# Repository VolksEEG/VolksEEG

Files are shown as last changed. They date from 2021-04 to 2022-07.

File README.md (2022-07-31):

# VolksEEG: Acheiving the Promise of Open Source Medical Devices

In a nutshell...

* *The VolksEEG project is creating an open-source
electroencephalogram (EEG) machine, fully-functional for clinical or research use.*

* *The final device will obtain clearance by the USA FDA, and CE marking
(the equivalent of FDA clearance in the EU).*

* *Currently, no other
open-source electronic medical device (that we know of) has full regulatory clearance*

* *All hardware and software designs will be freely available ([free as in speech and as in beer](https://www.howtogeek.com/howto/31717/what-do-the-phrases-free-speech-vs.-free-beer-really-mean)).*

VolksEEG will be the first in a line of open-source medical
devices that will enable a quantum leap in device safety, cost reduction, and innovation.

To sign up for updates about the project, head to [volkseeg.org](https://volkseeg.org).

Here is a video showing the real-time display of 32 waveform channels, from a UI proof-of-concept application:

<https://user-images.githubusercontent.com/58418/132131736-32bca075-f591-47dc-b3fa-c07dddc95de6.mp4>

(The final device will display EEG channels rather than sine waves, of course.)

## Qs & As

You might have a few questions; we have answers, click on the links below to read the:

* [Why are open-source medical devices a good
idea?](#why-are-open-source-medical-devices-a-good-idea)

* [Medical devices? Do you actually know what you're doing?](#do-you-actually-know-what-you-are-doing)

* [Why an EEG machine?](#why-start-with-an-eeg-machine)

* [What needs to be done?](#what-needs-to-be-done)

* [How can I help?](#how-can-i-help)

* [Project planning](#Project-planning)

* [Wait... don't medical devices need to have full requirements and specifications before starting any development?](#where-are-the-detailed-requirements-and-specs)

---

## Why are open-source medical devices a good idea?

Open-source medical devices will provide increased safety, increased
innovation, and reduced device costs.

### Increased Safety

Like all devices, medical devices have become much more complex over
time. *Unlike* all devices, medical devices are often safety- or
life-critical.

As complexity increases, it becomes ever easier to overlook
small design flaws during development, often leading to recalls
later – each year, hundreds of thousands of devices are subject to Class
I recalls, the FDA’s most serious class of recall, reserved for issues
that could cause serious injury or death.

Design flaws are detected by *design reviews*. A core challenge of medical
device safety is ensuring the adequacy of design reviews – both in the
person-hours spent, and the expertise of the reviewers. While design
reviews of proprietary medical devices typically involve only a handful
of reviewers, open-source devices can leverage the eyeballs of myriad
reviewers with a wide variety of expertise; as stated in *The Cathedral
and the Bazaar,* "given enough eyeballs, all bugs are shallow".

### Increased Innovation

Innovation in medical devices is painstakingly slow – compared to
devices from decades ago, most of today’s devices may have more
convenience features, but by-and-large their core functionality is the
same as it was decades ago.

There are several structural issues that impede device innovation. One
of these is the barrier between device companies and
clinicians/researchers. By building proprietary systems using a
conventional profit-only model, manufacturers make it difficult or
impossible for researchers to try new techniques and technologies that
could lead to breakthroughs.

Open-source designs will accelerate innovative research in hospitals and
universities. Investigators will be able to access data from devices,
and even make changes to devices to test new concepts. (To ensure
safety, the FDA and all hospitals have strict rules around how altered
devices can be used.)

In fact... VolksEEG will contain essentially the same circuitry as will be
used in our clinical EEG, and will directly fill a currently-unmet need for research into making anesthesia safer.

### Reduced Device Costs

Medical devices are expensive. There are various reasons for this – some
of these contribute to better patient care, but many don’t. A simple
illustration of this can be seen in the title of a recent journal
article *Prices for Cardiac Implant Devices May Be Up To Six Times
Higher In The US Than In Some European Countries*\[1\]. Frankly, if
device companies couldn’t *profitably* sell devices for one-sixth the
cost… *they wouldn’t*.

Open-source designs will democratize medical devices, resulting in
substantially lower prices. While relatively few companies have the
ability to *design* devices which meet regulatory standards, many more can
manufacture them. A verified design can be adopted by multiple vendors
who otherwise would not be able to develop devices, and competition
reduces pricing. Open-source designs will also enable poorer countries
and NGOs to manufacture their own devices, cutting out costs added by
middle-men.

---

## Do You Actually Know What You Are Doing?

The founding members of VolksEEG are:

* [Bryan Glezerson](https://www.linkedin.com/in/bryan-glezerson-ba71221a9/), a neurosurgical anesthesiologist (Bryan add stuff here).

* [Alan Cohen](https://www.linkedin.com/in/meddev/), an engineer with decades of experience in medical device development (including obtaining FDA clearance and CE marking). Alan is also the author of the book [ProtoType to Product: A Practical Guide for Getting to Market](https://smile.amazon.com/Prototype-Product-Practical-Getting-Market/dp/144936229X/ref=cm_cr_arp_d_product_top?ie=UTF8).

VolksEEG development will result in a safe design which
conforms to US and EU regulations – no different than any other
commercial medical device. Project participants will gain some knowledge
and experience in the medical device design/development processes.

---

## Why start with an EEG machine?

There are two major reasons for an EEG machine being our first product:

### Immediate Need

(Bryan writes this)

## Low-hanging fruit

An EEG machine is relatively simple compared to many other medical
devices, making it a good candidate for a first effort in open-source
devices:

1. Chips are available, e.g. the ADS1299 that we’re using, which are
    purpose-built for EEG use; they are essentially EEGs-on-a-chip that
    greatly reduce the effort needed to develop a full device. These
    components are at the heart of many proprietary EEGs.

2. EEG machines are a lower safety risk than other sophisticated
    medical devices, such as vital signs monitors and infusion pumps. A
    fundamental principal of medical device development is that effort
    should be based on risk. At the start of a project, potential risks
    are identified then addressed in development. Fewer potential risks
    translates into less effort to assure safety.

---

## What needs to be done?

VolksEEG development will have several phases. The first will result in
a “protoduction”\[2\] device to be used for EEG research. The second
will result in a reference design for a full, FDA-clearable device.

A basic block diagram of the prototype system architecture is below:

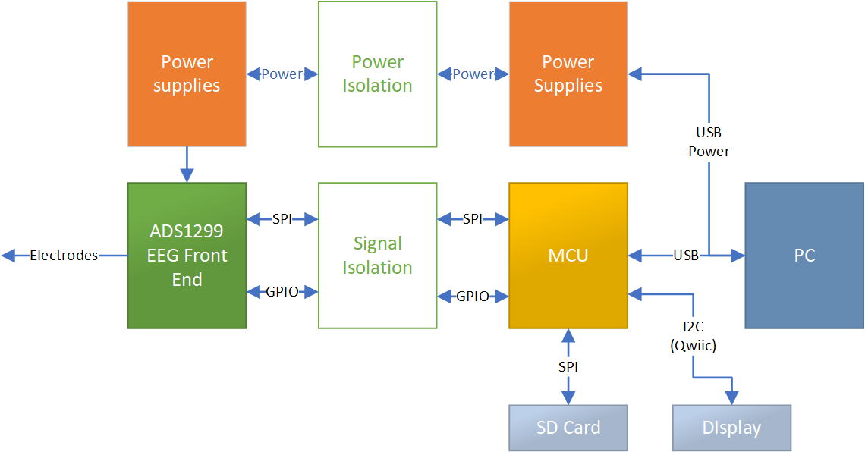
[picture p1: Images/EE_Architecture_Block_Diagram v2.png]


Other relevant information for nerds ☺️:

* MCU is a nrf52840. Firmware is currently written in Arduino, but
we’ve not yet decided what it will ultimately be. C? C++? Arduino?
Mbed? Also we might want to add an RTOS. Or we might not.

* The MCU and electronics support Bluetooth and NFC – we’re not particularly planning to use these initially, but we like the idea of being able to enable it later by flashing a firmware update.
* The SD card will contain EEG waveforms as standard \*.edf files.For test puposes these files can be read over USB and will appear to the PC application as "real" EEG waveforms.
* The PC software is being developed in C\#, a language that makes good tradeoffs between performance and software reliability.

---

## How can I help?

Development of this prototype breaks down into the following major
tasks:

* Electronics: this is currently staffed
* Firmware: we can use some help
* Software: Several proof-of-concept applications have been written to demonstrate concepts such as reading the serial port at
sufficiently-high speeds, writing 32 real-time waveforms to the
screen in C\#/Windows, and so forth. The next step is to build
the Windows-based spplication software using best practices,
and we would definitely appreciate some help with this.

* Cybersecurity. We could use expertise/help, mainly on the embedded side of things.
* Mechanical: designing and fabricating enclosures. This will be
fairly low effort to start, probably 3D printed. Later we'll likely
use injection molding.
* Regulatory: we have this reasonably under control, but welcome experienced help.
* Quality: this activity will ramp up over time, and we can use some help in writing documentation.

On the software, writing code work we can use a hand in:

* Working with doctors and technicians to understand and document workflow so our software can work the way our customers want.

* UI/UxD design.

Some non-engineering help we could use:

* Web site development
* Social media
* Fundraising
* Business development
* Legal
* Business issues
* IP issues

<!-- end list -->

---

## Where are the detailed requirements and specs?

The short story is that our initial effort will be a highly-functional prototype, not a medical device.

When a medical device is cleared by the FDA, it's required that there be
detailed requirements and specifications, and that development and testing
has proceeded deliberately to meet those requirements and specifications.

Medical device development uses relatively-heavyweight development processes
(i.e., there's a good bit of documentation, traceability matrices, etc) that
the FDA generally refers to as design controls. If development only proceeds
after writing and reviewing formal requirements/architecture/specs etc., we run
the risk of finding technical surprises that will cause us to back up and update
those requirements/architecture/specs that we worked so hard on. So, to avoid
wasted effort in creating requirements/architecture/specs that might get changed
later, it often makes sense to start by building a fairly-functional prototype
without using full medical-grade design controls, then once that's working to
circle back and redo the process using design controls. This usually ends up
reusing the designs produced during the prototype build, but now we document
and otherwise control them properly.

---

## Endnotes

1. Wenzl, Martin, and Elias Mossialos. “Prices For Cardiac Implant
   Devices May Be Up To Six Times Higher In The US Than In Some
   European Countries.” *Health Affairs*, vol. 37, no. 10, Oct. 2018,
   pp. 1570–77, doi:10.1377/hlthaff.2017.1367.

2. *Protoduction* refers to a device that is somewhere between
    prototype and production devices: far enough along that it can be
    used for its intended use, but not a fully-developed commercial
    product. Production quantities are typically low, in the ones or
    tens.

## For more information on VolksEEG (beyond this readme)

* Further technical details may be found on [our wiki](https://github.com/VolksEEG/VolksEEG/wiki).

* The start of a detailed project overview may be found [here](https://1drv.ms/w/s!AvEzNsBMxiAcpMBu5GTByJBZlJbeDA?e=k30pK4).

* Our repositories may be found on Github [here](https://github.com/VolksEEG/).

* The Firmware repository may be found [here](https://github.com/VolksEEG/eeg-device-firmware).

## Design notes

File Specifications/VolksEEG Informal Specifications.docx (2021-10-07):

# VolksEEG Specifications

# Anesthesia Research Model

- 8 leads
- Amenable to approval by investigational review boards (IRBs)

## Performance

In general, the device will conform to IEC 60601-2-26: Particular requirements for the basic safety and essential performance of electroencephalographs. The standard defines minimum performance and testing:

Requirement | Subclause
Accuracy of amplitude and rate of variation Input dynamic range and differential offset voltage Input noise Frequency response Common mode rejection Indication of invalid data | 201.12.1.102 201.12.1.103 201.12.1.104 201.12.1.105 201.12.1.106 201.12.4.101

<<We should add some actual values from the standard>>

Note: we generally assume that the ADS1299 IC will do virtually all of the “heavy lifting” in meeting these. But we should review, and test per the standard’s test procedures.

## Safety

The system will conform with all mandatory electrical safety clauses in IEC 60601-2-26, and in linked standards (e.g., IE60601-1). It may conform to optional clauses e.g., protection against defibrillation.

## Other regulatory

The system should conform to the following standards for electromagnetic compatibility (EMC), including emissions and immunity:

- IEC 60601-1-2 General requirements for basic safety and essential performance - Collateral Standard: Electromagnetic disturbances - Requirements and tests
- FCC standards for intentional and non-intentional radiators. The former is necessary to accommodate Bluetooth, and will likely be met by using a pre-certified module.

## Power

The system may be powered by:

- USB (micro B connector, either a USB power supply or data connection.
- Inbuilt rechargeable battery, UL-approved, that can power the system for XXX hours when fully charged

## Communications

## Physical

The device should:

- be splash-proof (IPX-4)
- not have sharp corners

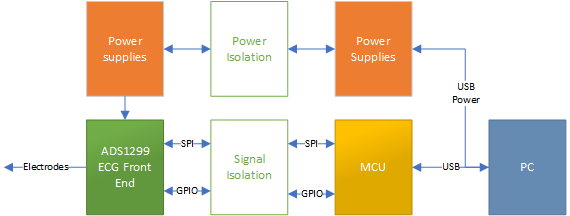
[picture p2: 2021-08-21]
Images/EE Architecture Block DIagram 2.png

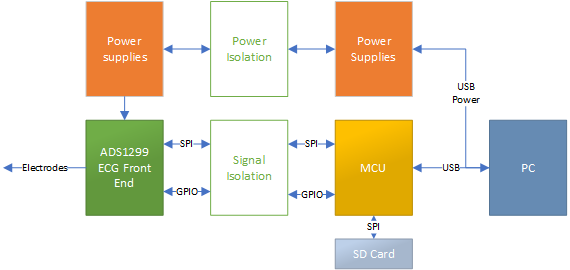
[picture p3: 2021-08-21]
Images/EE Architecture Block DIagram 3.png

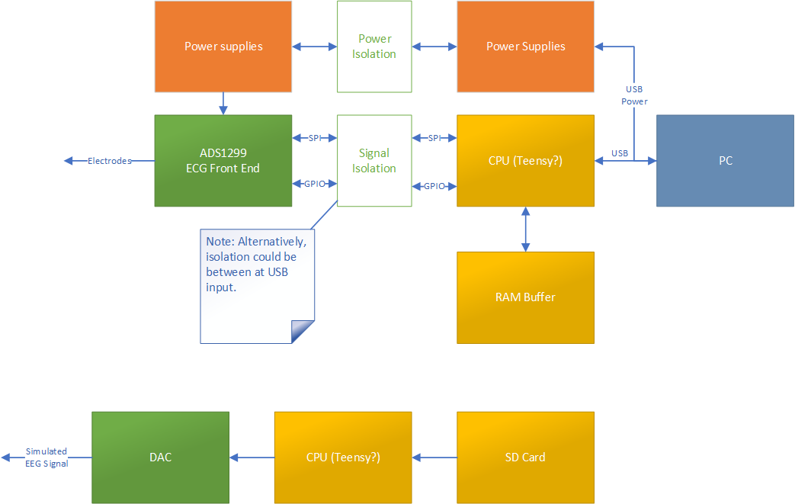
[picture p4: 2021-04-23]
hardware/EE Architecture Block Diagram.png

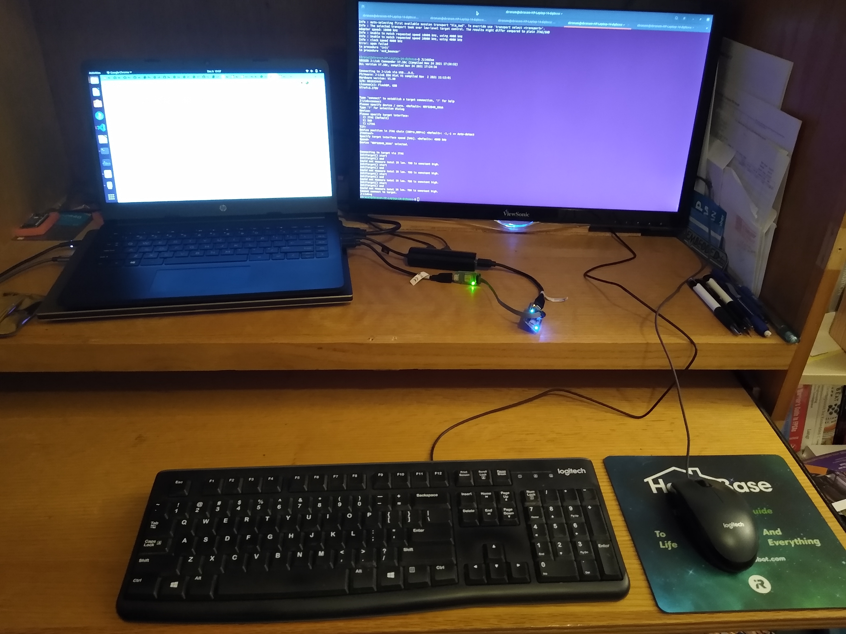
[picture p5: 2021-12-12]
Images/rust-adafruit-feather-express-workstation.jpg

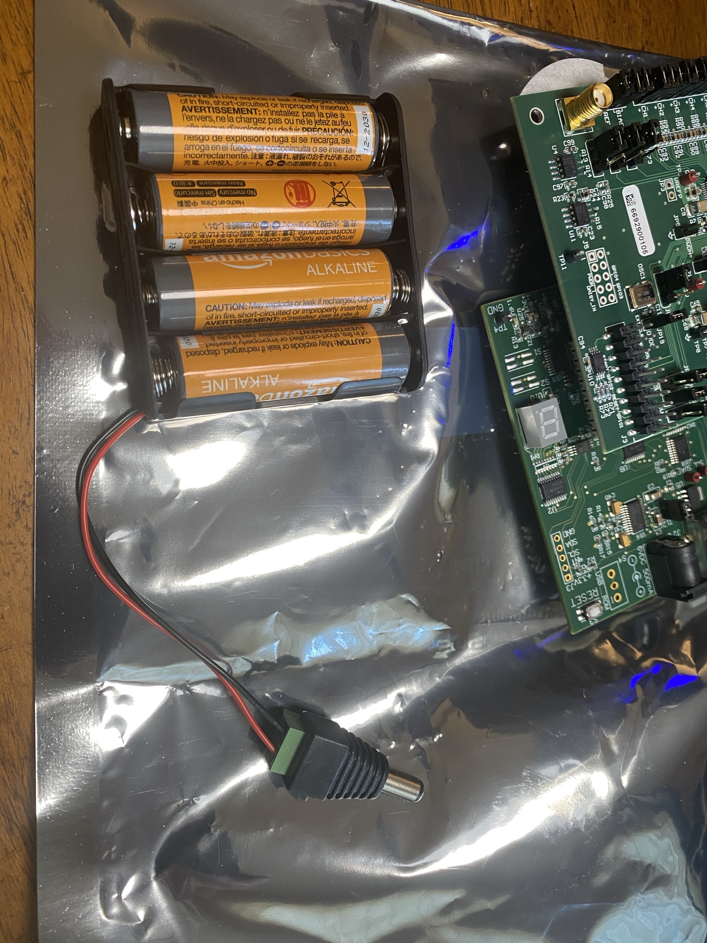
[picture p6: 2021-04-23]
Images/ADS1299EEG-PDK_Power_Supply.jpeg

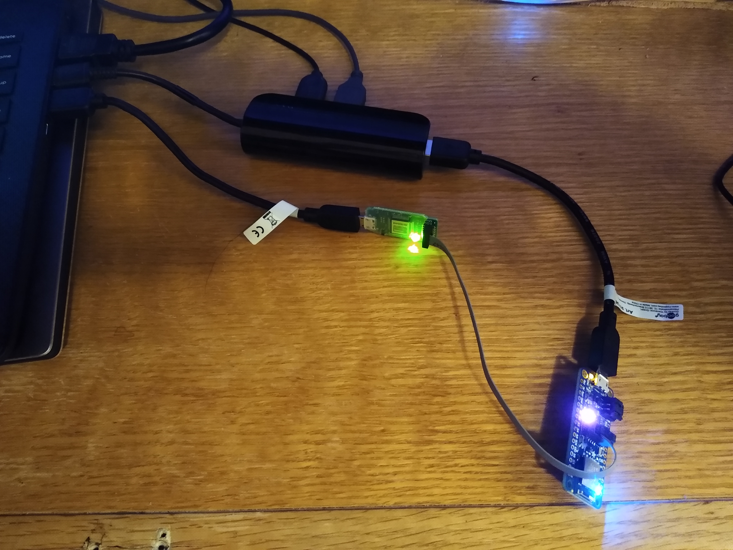
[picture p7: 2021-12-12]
Images/rust-adafruit-feather-express-board-jlink.jpg

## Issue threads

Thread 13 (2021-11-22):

### ISSUE TITLE
Question on the number of channels

### ISSUE THREAD

**Issue by thiswillbeyourgithub** [VolksEEG/VolksEEG#13]
Hi,

I have been following your github for some time now and am really eager to see what comes out of it :)

My question is : given that you first plan on creating an 8 channel version, how hard do you expect it would be to extend the project to support 16 or more channels? Is it simply a matter of duplicating the electronics or is it vastly more complex?

Context: I am a med student and python dev with very basic understanding of electronics so I wanted your take on this.

Thanks!

**Comment by alcohen** [comment]
In _theory_ it's not  big deal - mostly just scaling the electronics. The ADS1299 chip at the heart of VolksEEG has a daisy-chain mode to add devices and everything syncs up/behaves.

**Comment by thiswillbeyourgithub** [comment]
Thank you very much :).

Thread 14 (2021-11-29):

### ISSUE TITLE
Question on expected price of unit

### ISSUE THREAD

**Issue by thiswillbeyourgithub** [VolksEEG/VolksEEG#14]
Hi, it's me again :)

I was planning on buying a headset from openBCI in a few months but I heard about your project.

Being not that rich and with a very specific use case in mind, I am wondering if it would not be better to wait for *your* device to be fully prototyped if it was *substancially* cheaper than openBCI's headset.

So my question is: could you give me a range of expected unit price to your 8 channel version? Either to buy from you or to source myself (I'm talking mostly electronics and electrodes, I can deal with making the headset or DIYing missing stuff, but I can't write the firmware :/).

Looking at OpenBCI's shop I'm seeing a bare minimum of $850:
* Cython board (8 channel): $749
* cables and dry electrodes: $90

I understand that you're project is not directly aimed at consumers and is very early but I really have no idea if your aiming at the same kind of price or 5 times less or 5 times more :)

Thanks!

**Comment by alcohen** [comment]
Our primary "use case" for sales is for studies by researchers at institutions that have an IRB (Institutional Review Board).

We haven't yet internally discussed and made a decision about whether or how to sell units for use outside of that scenario. 

However, since this is open source, you could build it yourself. The parts cost, less PCBs, will likely be in the $300-$400 range (without electrodes) plus a Windows PC. PCBs should be under $100.

I hope that's helpful!

**Comment by thiswillbeyourgithub** [comment]
Thank you very much, this is very helpful.

I see you mentionning windows in the repo but I am on linux. Although your main app will be on windows, do you intend to make at least a minimal API that would be cross platform? Similar to OpenBCI's python API.

I don't really need a GUI, I'm mostly after an API to access data in realtime for machine learning.

Implementing a linux API myself is beyond my skills but if you supplied one I would gladly create the first community GUI / software suite :)

But in the end, OpenBCI already has a cross platform software, have you considered forking their app or making your prototype compatible with their software? Wouldn't that speed up your project?

Thanks :)

**Comment by rtullybarr** [comment]
Hey!

I'm working on the desktop software side - we're currently using WPF for the GUI, which is not itself cross-platform, but we're using .NET core for all the actual data capture and processing. This should open up the ability to have a cross-platform API.

I'll definitely look at OpenBCI, as I wasn't aware of its existence before now! It sounds beneficial to at least look into making our work compatible with it.

**Comment by thiswillbeyourgithub** [comment]
Hi!

Glad to hear I was useful in making you discover their stuff :). I am surprised that you had not heard of it as they are the top results when you search for "open source EEG" and are *approved* (or something like that) by the FDA. Doesn't that make them a direct competitor? Does that change anything to your endeavor? If not why not? :)

Regarding your last question:
I'm going to admit right away that I'm a beginner regarding EEG. But I'm a med student with a clear interest toward it, a python developper and very interested in AI.

* Hence what I would be after is at least being able to access raw data in an accessible format. For example, in [this video at 9min30s](https://www.youtube.com/watch?v=Dgo7F-lpyYE) youtuber "sentdex" use a simple python import statement and gets an output. He then creates a little script to make sure the data dumps comes with a consistent timing. If I have this I can probably manage to get what I need to do machine learning stuff, plot things etc. I will of course make everything open source and contribute to the community :)
* BUT if you want to and can go the extra mile, making your device compatible with their software suite (same API, same GUI, same everything) will not hurt.

In the end, I don't want to interfere with the scope of the project. I can manage with the bare minimum (API with raw data), and would definitely appreciate it if your project could resuse already existing projects.

(btw: they are compatible with LSL too #16)

**Comment by alcohen** [comment]
Hi there!

The primary difference is that Volks EEG has the goal of becoming a full-fledged FDA-cleared device. Our first generation device will be similar to theirs as it will be appropriate for research, although it will prove out some new things.

Second iteration will be developed as a medical device, meeting FDA/EU regs.

That said, using the open BCI software front end as a milestone might make good sense, we should review the interface and see what the effort entails. 

In principle, it would also be good for our own front end to support multiple output formats, which should be do-able over time.

Thanks for your input and questions, they are very helpful!

**Comment by thiswillbeyourgithub** [comment]
Thank you for your answer.

I can't wait to see what comes out of your project :)

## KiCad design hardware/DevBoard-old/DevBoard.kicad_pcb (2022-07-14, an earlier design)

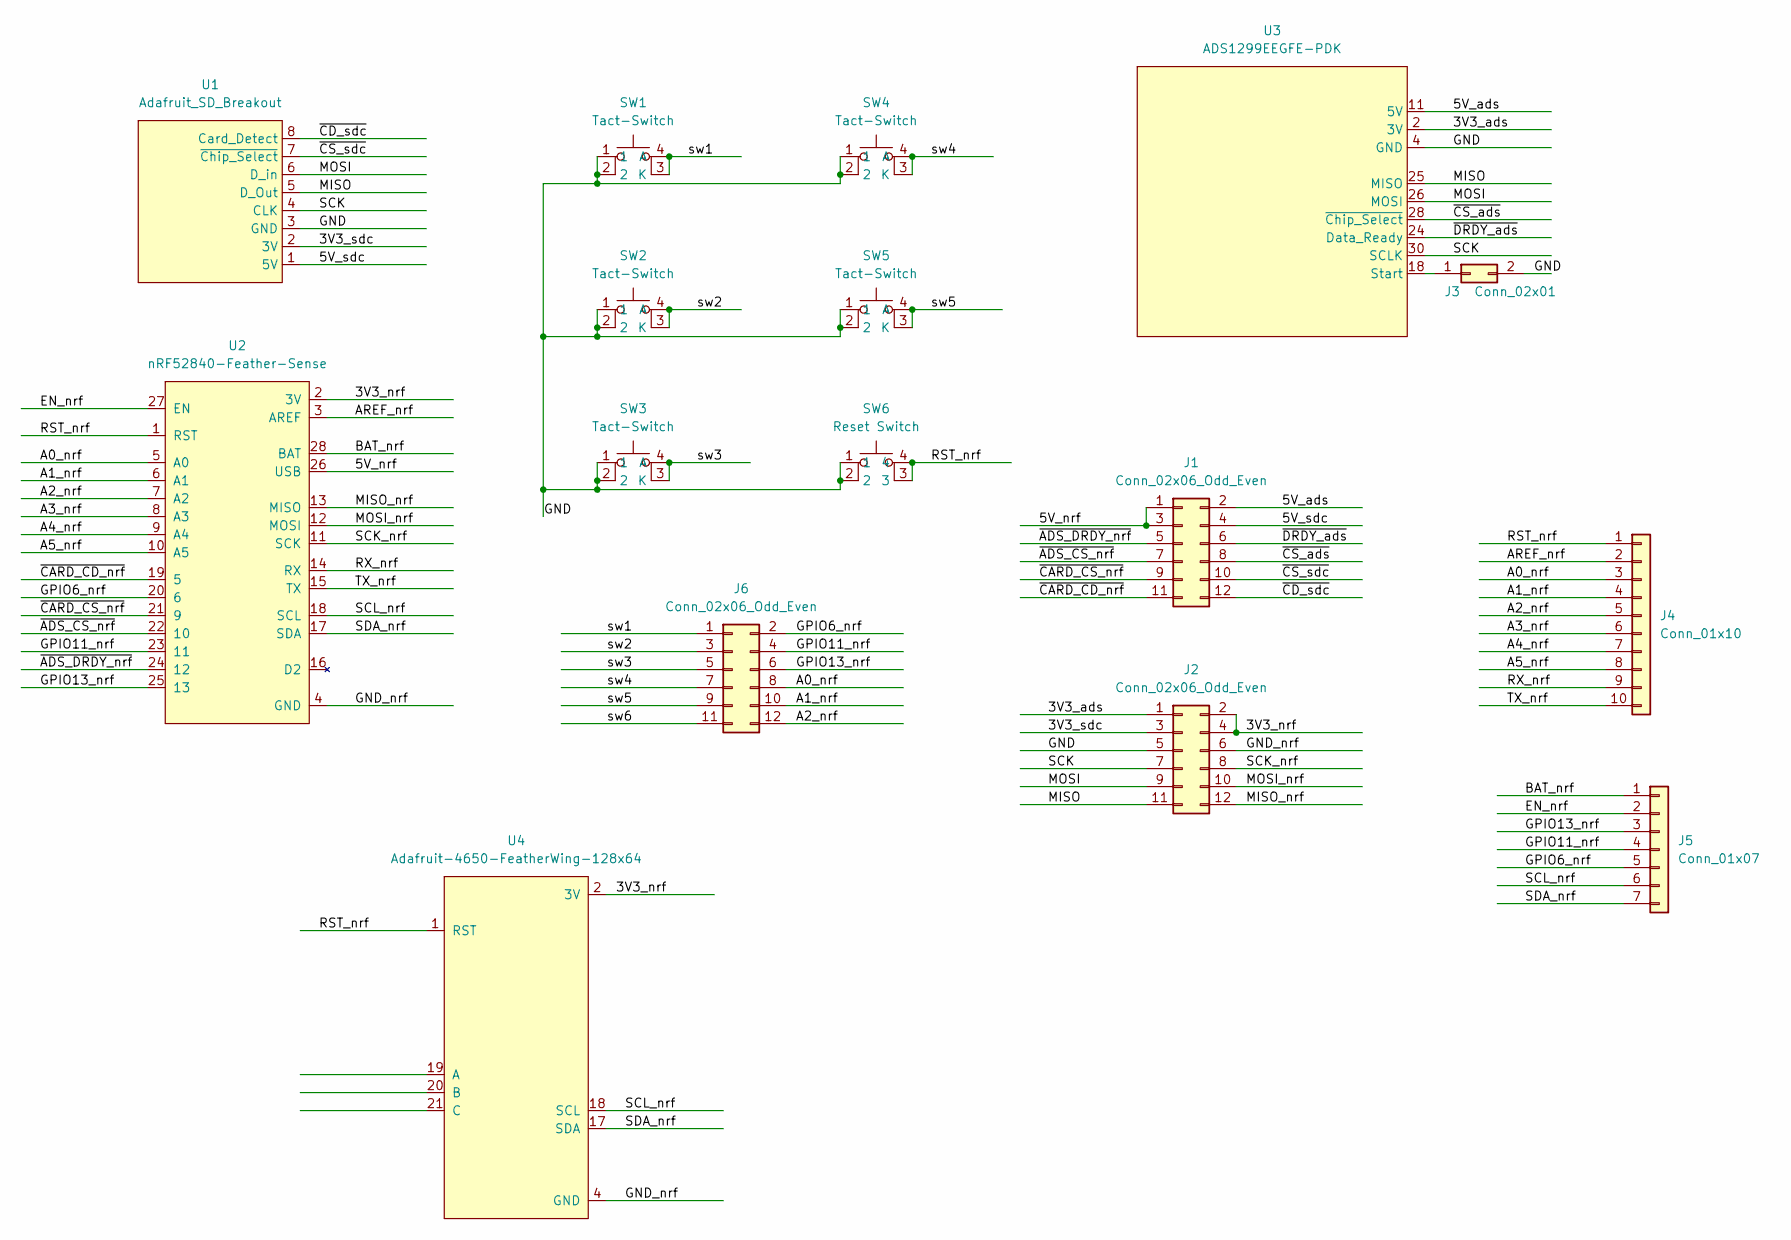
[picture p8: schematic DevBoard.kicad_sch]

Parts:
J1, J2: Conn_02x06_Odd_Even; PinHeader_2x06_P2.54mm_Vertical
J3: Conn_02x01; PinHeader_1x02_P2.54mm_Vertical
J4: Conn_01x10; PinHeader_1x10_P2.54mm_Vertical
J5: Conn_01x07; PinHeader_1x07_P2.54mm_Vertical
J6: Conn_02x06_Odd_Even; 6-Jumper Header
SW1, SW2, SW3, SW4, SW5: Tact-Switch; Sparkfun Tactile Switch
SW6: Reset Switch; Sparkfun Tactile Switch
U1: Adafruit_SD_Breakout; Part Number 254
U2: nRF52840-Feather-Sense; nRF52840_Feather_Sense
U3: ADS1299EEGFE-PDK
U4: Adafruit-4650-FeatherWing-128x64; nRF52840_Feather_Sense

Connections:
/3V3_ads: J2.1, U3.2 (3V)
/3V3_nrf: J2.2, J2.4, U2.2 (3V), U4.2 (3V)
/3V3_sdc: J2.3, U1.2 (3V)
/5V_ads: J1.2, U3.11 (5V)
/5V_nrf: J1.1, J1.3, U2.26 (USB)
/5V_sdc: J1.4, U1.1 (5V)
/A0_nrf: J4.3, J6.8, U2.5 (A0)
/A1_nrf: J4.4, J6.10, U2.6 (A1)
/A2_nrf: J4.5, J6.12, U2.7 (A2)
/A3_nrf: J4.6, U2.8 (A3)
/A4_nrf: J4.7, U2.9 (A4)
/A5_nrf: J4.8, U2.10 (A5)
/AREF_nrf: J4.2, U2.3 (AREF)
/BAT_nrf: J5.1, U2.28 (BAT)
/EN_nrf: J5.2, U2.27 (EN)
/GND: J2.5, J3.2, SW1.1, SW1.2, SW2.1, SW2.2, SW3.1, SW3.2, SW4.1, SW4.2, SW5.1, SW5.2, SW6.1, SW6.2, U1.3 (GND), U3.4 (GND)
/GND_nrf: J2.6, U2.4 (GND), U4.4 (GND)
/GPIO6_nrf: J5.5, J6.2, U2.20 (6)
/GPIO11_nrf: J5.4, J6.4, U2.23 (11)
/GPIO13_nrf: J5.3, J6.6, U2.25 (13)
/MISO: J2.11, U1.5 (D_Out), U3.25 (MISO)
/MISO_nrf: J2.12, U2.13 (MISO)
/MOSI: J2.9, U1.6 (D_in), U3.26 (MOSI)
/MOSI_nrf: J2.10, U2.12 (MOSI)
/RST_nrf: J4.1, SW6.3, SW6.4, U2.1 (RST), U4.1 (RST)
/RX_nrf: J4.9, U2.14 (RX)
/SCK: J2.7, U1.4 (CLK), U3.30 (SCLK)
/SCK_nrf: J2.8, U2.11 (SCK)
/SCL_nrf: J5.6, U2.18 (SCL), U4.18 (SCL)
/SDA_nrf: J5.7, U2.17 (SDA), U4.17 (SDA)
/TX_nrf: J4.10, U2.15 (TX)
/sw1: J6.1, SW1.3 (K), SW1.4 (A)
/sw2: J6.3, SW2.3 (K), SW2.4 (A)
/sw3: J6.5, SW3.3 (K), SW3.4 (A)
/sw4: J6.7, SW4.3 (K), SW4.4 (A)
/sw5: J6.9, SW5.3 (K), SW5.4 (A)
/sw6: J6.11
/~ADS_CS_nrf: J1.7, U2.22 (10)
/~ADS_DRDY_nrf: J1.5, U2.24 (12)
/~CARD_CD_nrf: J1.11, U2.19 (5)
/~CARD_CS_nrf: J1.9, U2.21 (9)
/~CD_sdc: J1.12, U1.8 (Card_Detect)
/~CS_ads: J1.8, U3.28 (~Chip_Select)
/~CS_sdc: J1.10, U1.7 (~Chip_Select)
/~DRDY_ads: J1.6, U3.24 (Data_Ready)
unnamed: J3.1, U3.18 (Start)

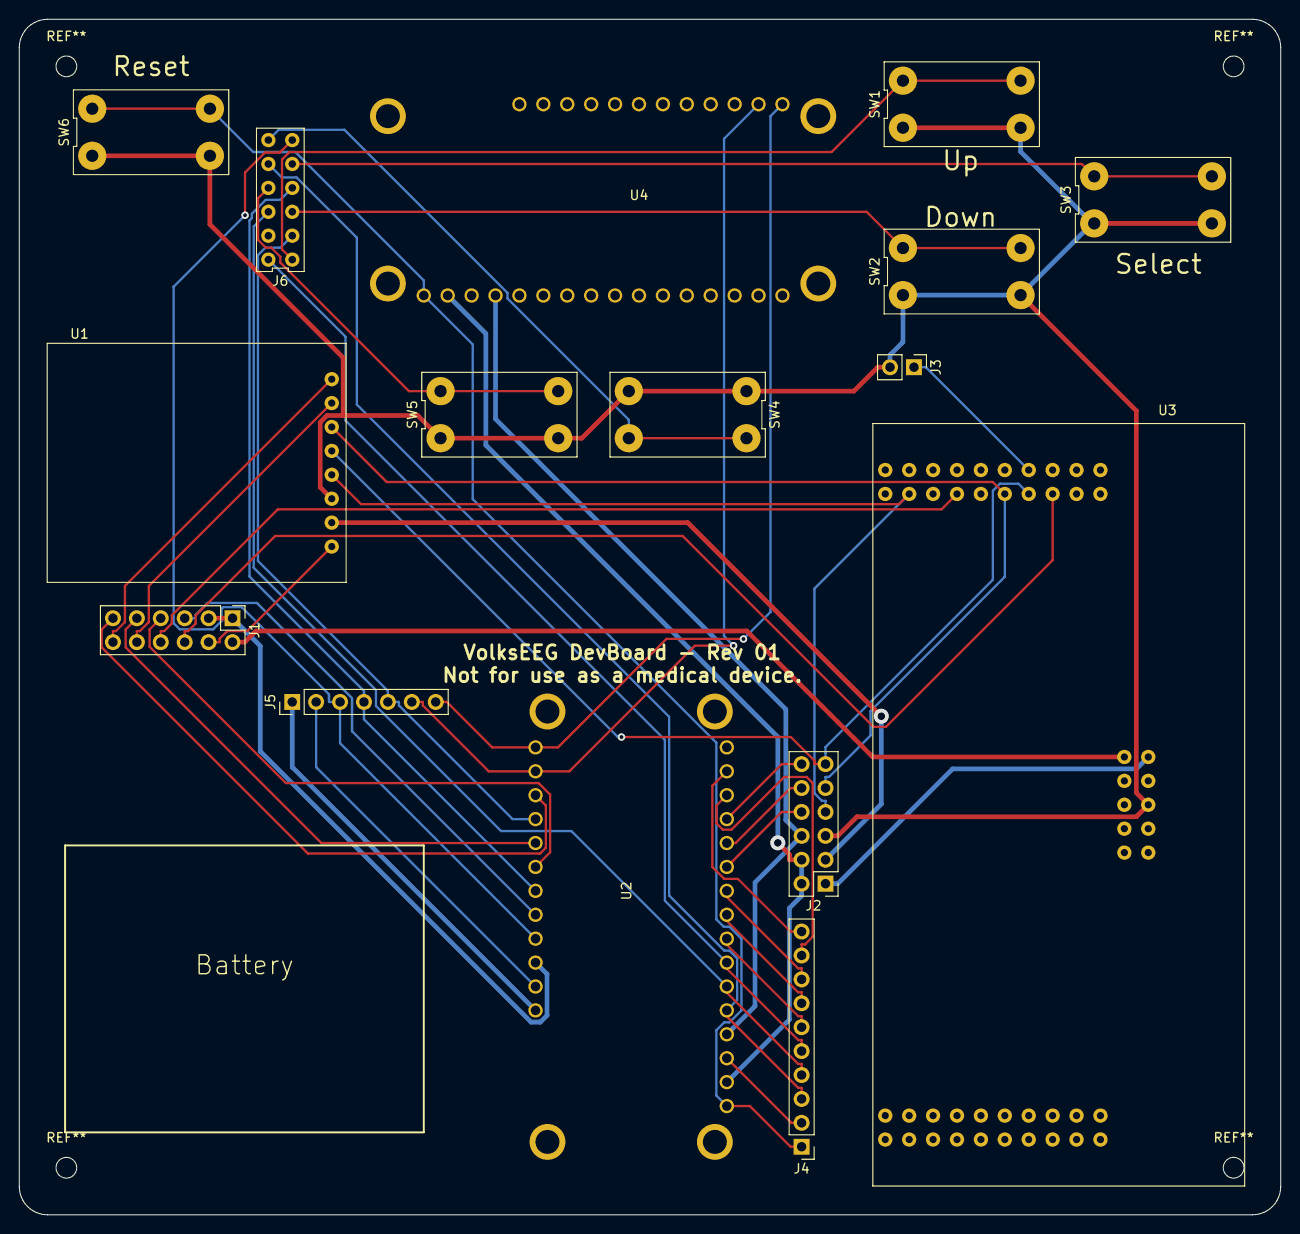
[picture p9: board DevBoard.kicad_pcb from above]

Board: 2 copper layers, 134.0 x 127.0 mm, 16 parts (0 on the bottom side), 45 nets.

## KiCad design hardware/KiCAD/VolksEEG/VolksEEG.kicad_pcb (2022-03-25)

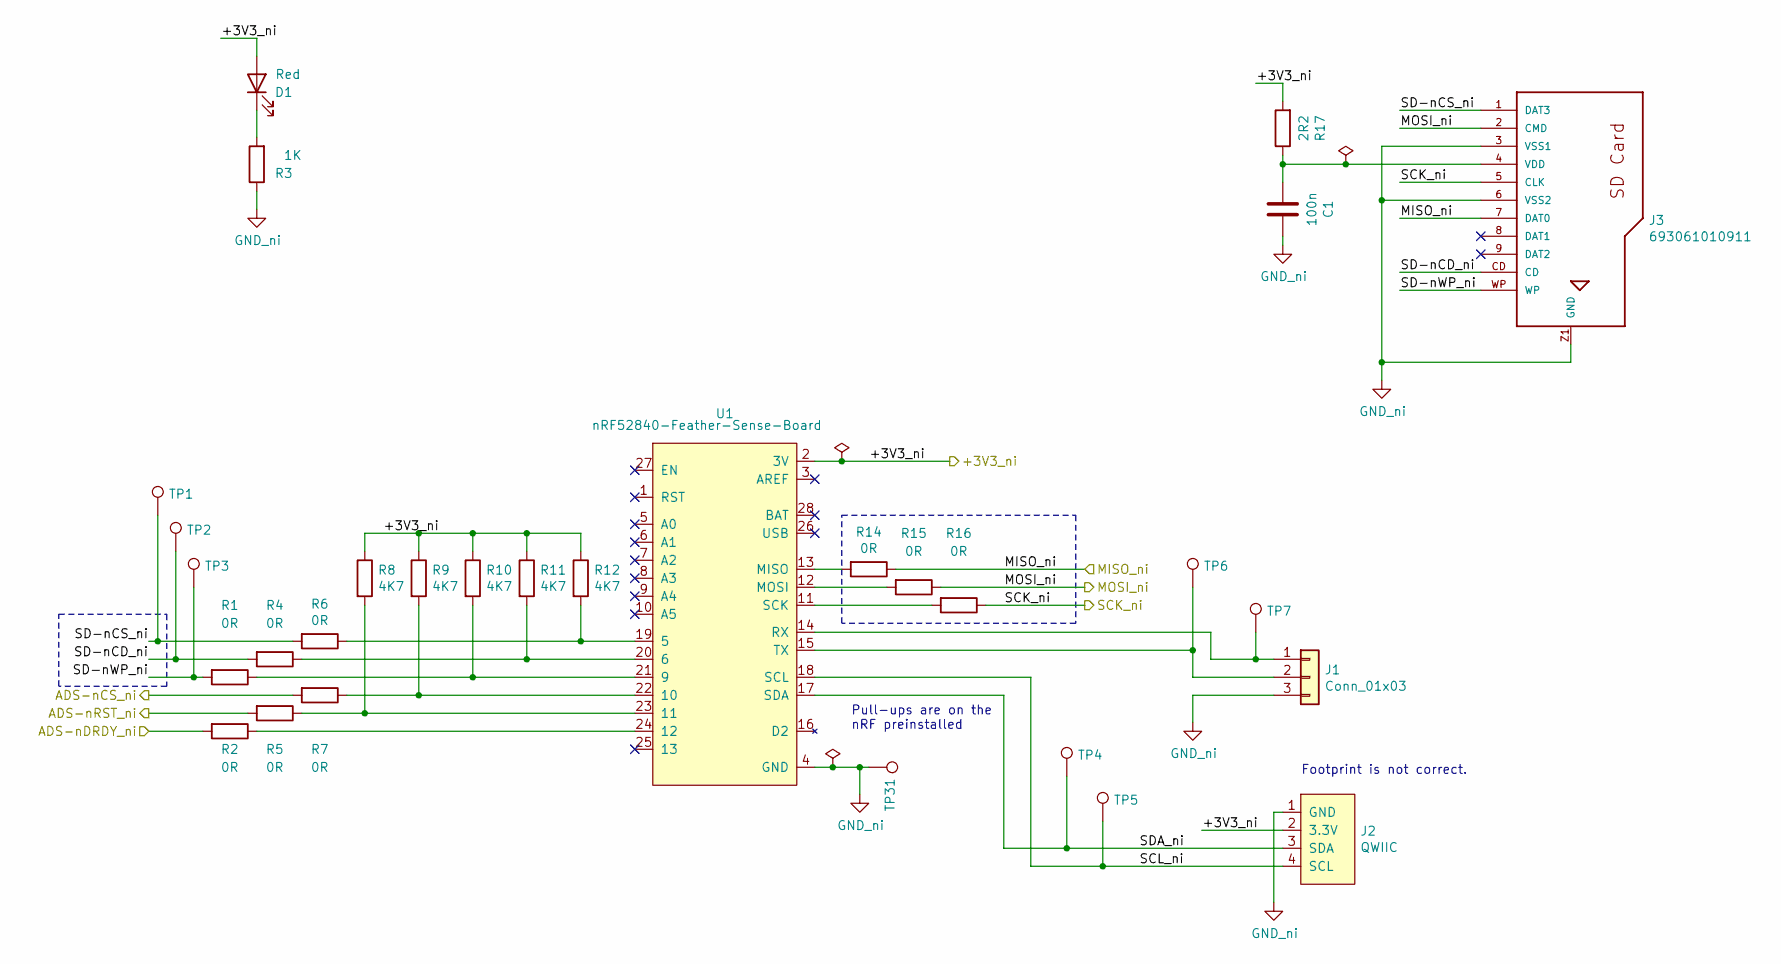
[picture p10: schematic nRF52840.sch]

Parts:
C1: 100n; C_0603_1608Metric_Pad1.08x0.95mm_HandSolder; Part Number CL21B104KACNNNC
D1: Red; LED_0603_1608Metric_Pad1.05x0.95mm_HandSolder; Part Number VFHR1111C-3BY2A-TR
J1: Conn_01x03; PinHeader_1x03_P2.54mm_Vertical; Part Number 640456-3
J2: QWIIC; PinHeader_1x04_P2.54mm_Vertical; Part Number 640456-4
J3: 693061010911; Part Number 693061010911
R1, R2, R4, R5, R6, R7, R14, R15, R16: 0R; R_0603_1608Metric_Pad0.98x0.95mm_HandSolder; Part Number TRR03EZPJ000
R3: 1K; R_0603_1608Metric_Pad0.98x0.95mm_HandSolder; Part Number RMCF0603FG1K00
R8, R9, R10, R11, R12: 4K7; R_0603_1608Metric_Pad0.98x0.95mm_HandSolder; Part Number RMCF0603FT4K70
R17: 2R2; high_power_chip_resistor; Part Number 35502R2JT
TP1, TP2, TP3, TP4, TP5, TP6, TP7: TestPoint; TestPoint_Keystone_5010-5014_Multipurpose; Part Number N/A
TP31: TestPoint; TestPoint_Bridge_Pitch7.62mm_Drill1.3mm; Part Number N/A
U1: nRF52840-Feather-Sense-Board; nRF52840_Feather_Sense; Part Number 4516

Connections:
/Isolation/+3V3_ni: D1.2 (A), J2.2 (3.3V), R8.1, R9.1, R10.1, R11.1, R12.1, R17.2, U1.2 (3V); also elsewhere on the board
/Isolation/MISO_ni: J3.7 (DAT0), R14.1; also elsewhere on the board
/Isolation/MOSI_ni: J3.2 (CMD), R15.1; also elsewhere on the board
/Isolation/SCK_ni: J3.5 (CLK), R16.1; also elsewhere on the board
/nRF52840 Feather Sense Express Board/ADS-nCS_ni: R7.2; also elsewhere on the board
/nRF52840 Feather Sense Express Board/ADS-nDRDY_ni: R2.2; also elsewhere on the board
/nRF52840 Feather Sense Express Board/ADS-nRST_ni: R5.2; also elsewhere on the board
/nRF52840 Feather Sense Express Board/SCL_ni: J2.4 (SCL), TP5.1, U1.18 (SCL)
/nRF52840 Feather Sense Express Board/SD-nCD_ni: J3.CD, R4.2, TP2.1
/nRF52840 Feather Sense Express Board/SD-nCS_ni: J3.1 (DAT3), R6.2, TP1.1
/nRF52840 Feather Sense Express Board/SD-nWP_ni: J3.WP, R1.2, TP3.1
/nRF52840 Feather Sense Express Board/SDA_ni: J2.3 (SDA), TP4.1, U1.17 (SDA)
GND: C1.1, J1.3, J2.1 (GND), J3.3 (VSS1), J3.6 (VSS2), J3.Z1 (GND), J3.Z2 (GND), R3.1, TP31.1, U1.4 (GND); also elsewhere on the board
unnamed: C1.2, J3.4 (VDD), R17.1
unnamed: D1.1 (K), R3.2
unnamed: J1.1, TP7.1, U1.14 (RX)
unnamed: J1.2, TP6.1, U1.15 (TX)
unnamed: R1.1, R10.2, U1.21 (9)
unnamed: R2.1, U1.24 (12)
unnamed: R5.1, R8.2, U1.23 (11)
unnamed: R7.1, R9.2, U1.22 (10)
unnamed: R4.1, R11.2, U1.20 (6)
unnamed: R6.1, R12.2, U1.19 (5)
unnamed: R14.2, U1.13 (MISO)
unnamed: R15.2, U1.12 (MOSI)
unnamed: R16.2, U1.11 (SCK)

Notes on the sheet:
Pull-ups are on the nRF preinstalled
Footprint is not correct.

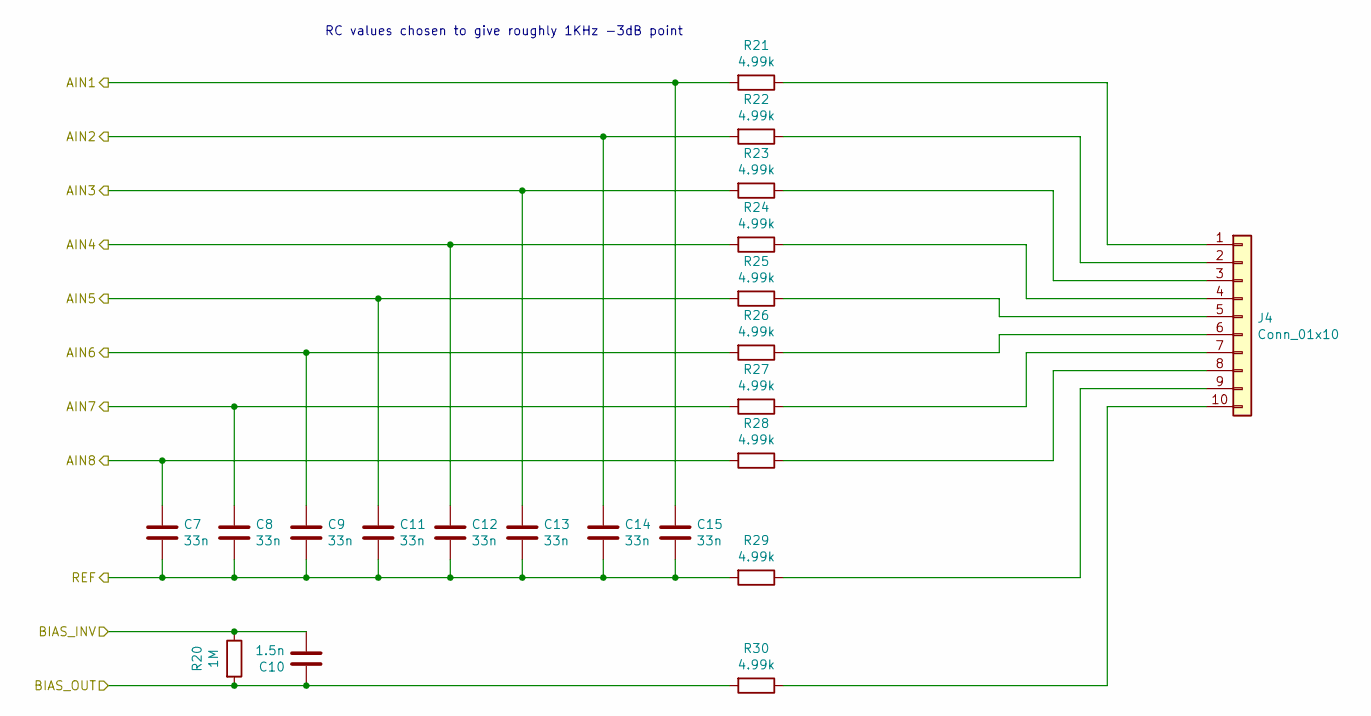
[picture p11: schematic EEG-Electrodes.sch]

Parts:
C7, C8, C9, C11, C12, C13, C14, C15: 33n; C_0805_2012Metric_Pad1.18x1.45mm_HandSolder; Part Number C0805C333F3GEC7210
C10: 1.5n; C_0603_1608Metric_Pad1.08x0.95mm_HandSolder; Part Number 08055A152FAT2A
J4: Conn_01x10; PinHeader_1x10_P2.54mm_Vertical; Part Number 1-640456-0
R20: 1M; R_0603_1608Metric_Pad0.98x0.95mm_HandSolder; Part Number CPF0603B1M0E1
R21, R22, R23, R24, R25, R26, R27, R28, R29, R30: 4.99k; R_0603_1608Metric_Pad0.98x0.95mm_HandSolder; Part Number RNCF0603TKY4K99

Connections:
/ADS1299/AIN1: C15.1, R21.2; also elsewhere on the board
/ADS1299/AIN2: C14.1, R22.2; also elsewhere on the board
/ADS1299/AIN3: C13.1, R23.2; also elsewhere on the board
/ADS1299/AIN4: C12.1, R24.2; also elsewhere on the board
/ADS1299/AIN5: C11.1, R25.2; also elsewhere on the board
/ADS1299/AIN6: C9.1, R26.2; also elsewhere on the board
/ADS1299/AIN7: C8.1, R27.2; also elsewhere on the board
/ADS1299/AIN8: C7.1, R28.2; also elsewhere on the board
/ADS1299/BIAS_INV: C10.2, R20.1; also elsewhere on the board
/ADS1299/BIAS_OUT: C10.1, R20.2, R30.2; also elsewhere on the board
/ADS1299/REF: C7.2, C8.2, C9.2, C11.2, C12.2, C13.2, C14.2, C15.2, R29.2; also elsewhere on the board
unnamed: J4.1, R21.1
unnamed: J4.2, R22.1
unnamed: J4.3, R23.1
unnamed: J4.4, R24.1
unnamed: J4.5, R25.1
unnamed: J4.6, R26.1
unnamed: J4.7, R27.1
unnamed: J4.8, R28.1
unnamed: J4.9, R29.1
unnamed: J4.10, R30.1

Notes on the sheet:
RC values chosen to give roughly 1KHz -3dB point

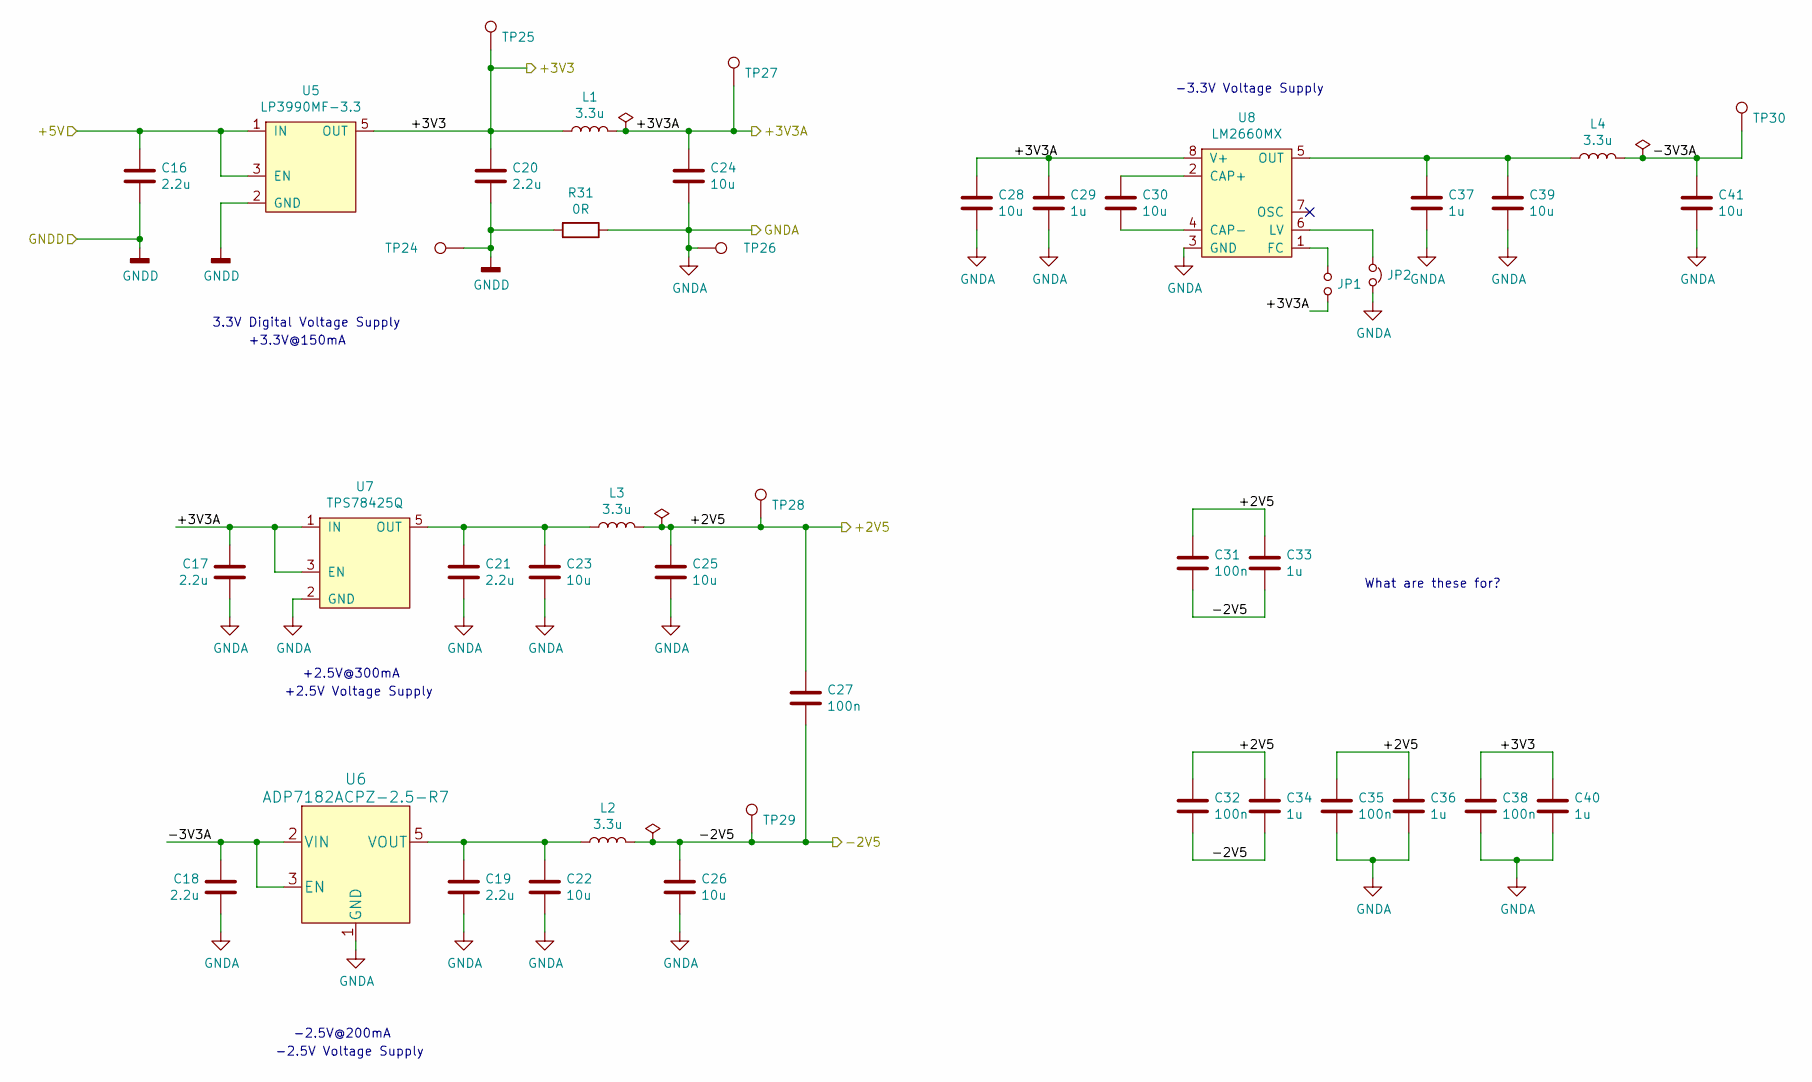
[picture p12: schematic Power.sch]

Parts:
C16, C17, C18, C19, C20, C21: 2.2u; C_0603_1608Metric_Pad1.08x0.95mm_HandSolder; Part Number CL21B225KAFNFNE
C22, C23, C24, C25, C26, C28, C30, C39, C41: 10u; C_0603_1608Metric_Pad1.08x0.95mm_HandSolder; Part Number CL21B106KPQNNNE
C27, C31, C32, C35, C38: 100n; C_0603_1608Metric_Pad1.08x0.95mm_HandSolder; Part Number CL21B104KACNNNC
C29, C33, C34, C36, C37, C40: 1u; C_0603_1608Metric_Pad1.08x0.95mm_HandSolder; Part Number CL21B105KAFNNNE
JP1: Jumper_NO_Small; SolderJumper-2_P1.3mm_Open_Pad1.0x1.5mm; Part Number N/A
JP2: Jumper_NC_Small; SolderJumper-2_P1.3mm_Bridged_Pad1.0x1.5mm; Part Number N/A
L1, L2, L3, L4: 3.3u; L_0805_2012Metric_Pad1.15x1.40mm_HandSolder; Part Number MLZ2012A3R3WTD25
R31: 0R; R_0603_1608Metric_Pad0.98x0.95mm_HandSolder; Part Number TRR03EZPJ000
TP24, TP26: TestPoint; TestPoint_Bridge_Pitch7.62mm_Drill1.3mm; Part Number N/A
TP25, TP27, TP28, TP29, TP30: TestPoint; TestPoint_Keystone_5010-5014_Multipurpose; Part Number N/A
U5: LP3990MF-3.3; SOT-23-5_HandSoldering; Part Number LP3990MF-3.3
U6: ADP7182ACPZ-2.5-R7; TSOT-23-5; Part Number ADP7182ACPZN-2.5R7
U7: TPS78425Q; SOT-23-5_HandSoldering; Part Number TPS78425QDBVRQ1
U8: LM2660MX; SOIC127P599X175-8N; Part Number LM2660MX

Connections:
/ADS1299 Power/+2V5: C25.1, C27.1, C31.1, C32.1, C33.1, C34.1, C35.1, C36.1, L3.2, TP28.1; also elsewhere on the board
/ADS1299 Power/+3V3: C20.1, C38.1, C40.1, L1.1, TP25.1, U5.5 (OUT); also elsewhere on the board
/ADS1299 Power/+3V3A: C17.1, C24.1, C28.1, C29.1, JP1.2, L1.2, TP27.1, U7.1 (IN), U7.3 (EN), U8.8 (V+); also elsewhere on the board
/ADS1299 Power/+5V: C16.1, U5.1 (IN), U5.3 (EN); also elsewhere on the board
/ADS1299 Power/-2V5: C26.1, C27.2, C31.2, C32.2, C33.2, C34.2, L2.2, TP29.1; also elsewhere on the board
/ADS1299 Power/-3V3A: C18.1, C41.1, L4.2, TP30.1, U6.2 (VIN), U6.3 (EN)
GNDA: C17.2, C18.2, C19.2, C21.2, C22.2, C23.2, C24.2, C25.2, C26.2, C28.2, C29.2, C35.2, C36.2, C37.2, C38.2, C39.2, C40.2, C41.2, JP2.2, R31.1, TP26.1, U6.1 (GND), U7.2 (GND), U8.3 (GND); also elsewhere on the board
GNDD: C16.2, C20.2, R31.2, TP24.1, U5.2 (GND); also elsewhere on the board
unnamed: C19.1, C22.1, L2.1, U6.5 (VOUT)
unnamed: C21.1, C23.1, L3.1, U7.5 (OUT)
unnamed: C30.1, U8.2 (CAP+)
unnamed: C30.2, U8.4 (CAP-)
unnamed: C37.1, C39.1, L4.1, U8.5 (OUT)
unnamed: JP1.1, U8.1 (FC)
unnamed: JP2.1, U8.6 (LV)

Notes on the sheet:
+2.5V Voltage Supply
+2.5V@300mA
-2.5V@200mA
-3.3V Voltage Supply
3.3V Digital Voltage Supply
-2.5V Voltage Supply
+3.3V@150mA
What are these for?

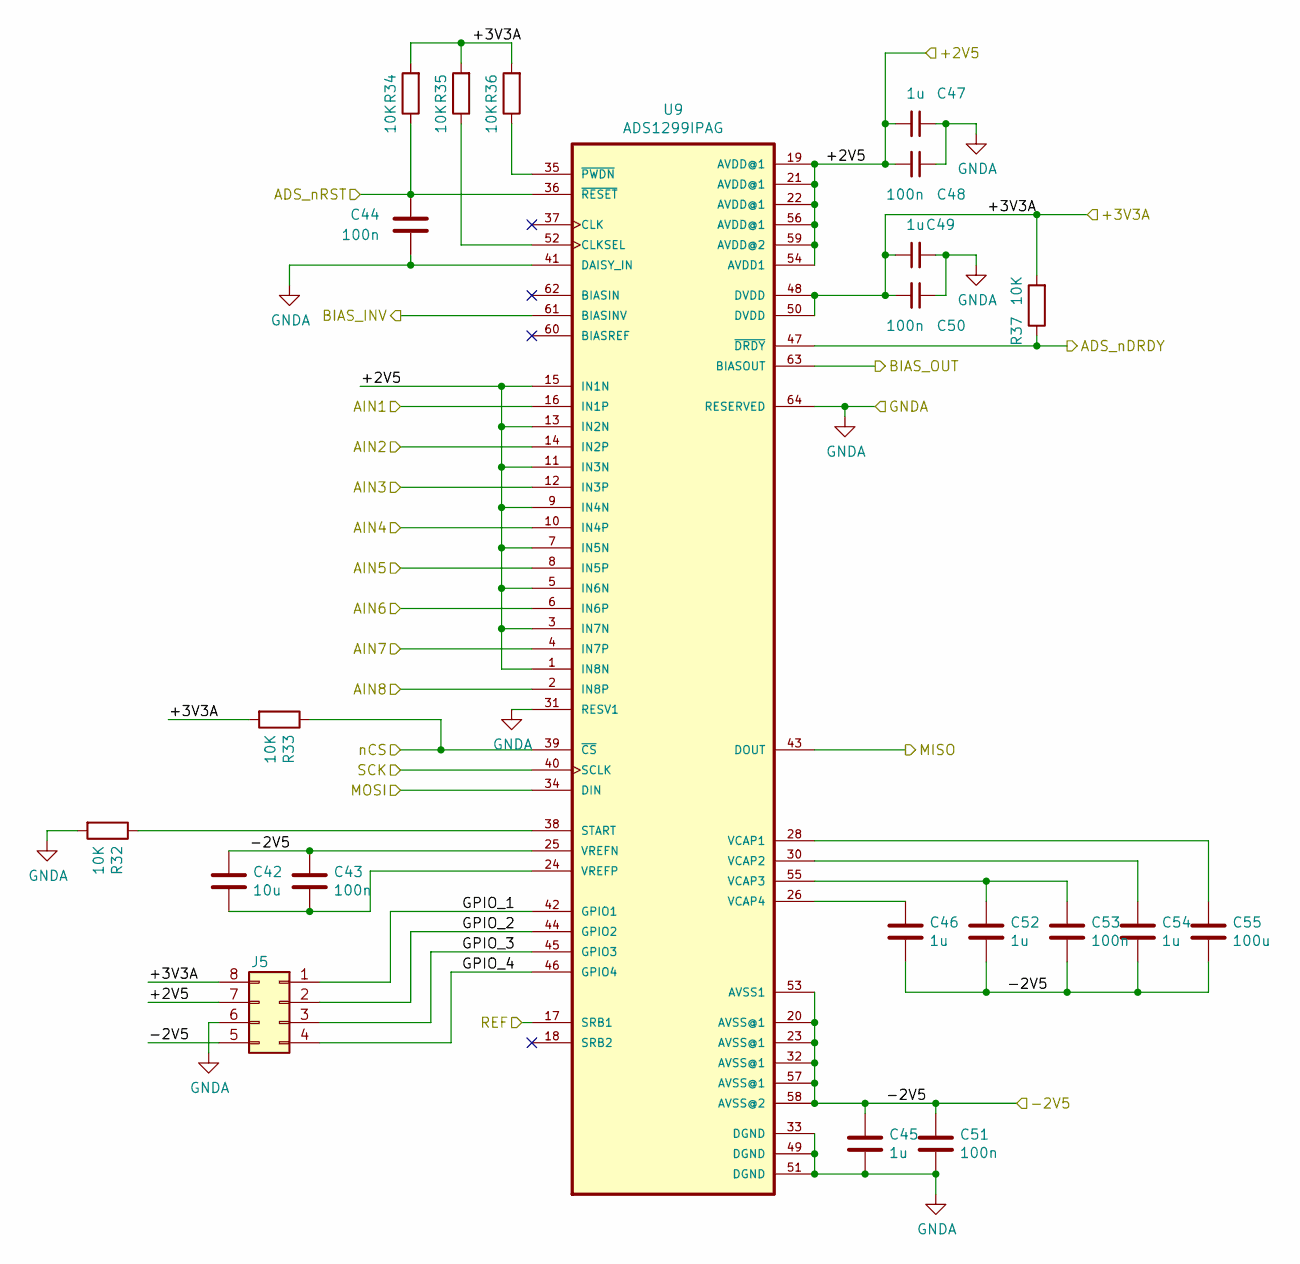
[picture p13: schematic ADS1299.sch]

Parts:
C42: 10u; C_0603_1608Metric_Pad1.08x0.95mm_HandSolder; Part Number CL21B106KPQNNNE
C43, C44, C48, C50, C51, C53: 100n; C_0603_1608Metric_Pad1.08x0.95mm_HandSolder; Part Number CL21B104KACNNNC
C45, C46, C47, C49, C52, C54: 1u; C_0603_1608Metric_Pad1.08x0.95mm_HandSolder; Part Number CL21B105KAFNNNE
C55: 100u; C_1210_3225Metric_Pad1.33x2.70mm_HandSolder; Part Number LMK325ABJ107MMHP
J5: Conn_02x04_Counter_Clockwise; PinHeader_2x04_P2.54mm_Vertical; Part Number 5-146256-4
R32, R33, R34, R35, R36, R37: 10K; R_0603_1608Metric_Pad0.98x0.95mm_HandSolder; Part Number RMCF0603JT10K0
U9: ADS1299IPAG; LQFP-64_10x10mm_P0.5mm; Part Number ADS1299IPAG

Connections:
/ADS1299 Power/+2V5: C47.2, C48.2, J5.7, U9.1 (IN8N), U9.3 (IN7N), U9.5 (IN6N), U9.7 (IN5N), U9.9 (IN4N), U9.11 (IN3N), U9.13 (IN2N), U9.15 (IN1N), U9.19 (AVDD@1), U9.21 (AVDD@1), U9.22 (AVDD@1), U9.54 (AVDD1), U9.56 (AVDD@1), U9.59 (AVDD@2); also elsewhere on the board
/ADS1299 Power/+3V3A: C49.1, C50.2, J5.8, R33.2, R34.2, R35.2, R36.2, R37.2, U9.48 (DVDD), U9.50 (DVDD); also elsewhere on the board
/ADS1299 Power/-2V5: C42.1, C43.1, C45.1, C46.2, C51.1, C52.2, C53.2, C54.2, C55.2, J5.5, U9.20 (AVSS@1), U9.23 (AVSS@1), U9.25 (VREFN), U9.32 (AVSS@1), U9.53 (AVSS1), U9.57 (AVSS@1), U9.58 (AVSS@2); also elsewhere on the board
/ADS1299/ADS_nDRDY: R37.1, U9.47 (~DRDY); also elsewhere on the board
/ADS1299/ADS_nRST: C44.2, R34.1, U9.36 (~RESET); also elsewhere on the board
/ADS1299/AIN1: U9.16 (IN1P); also elsewhere on the board
/ADS1299/AIN2: U9.14 (IN2P); also elsewhere on the board
/ADS1299/AIN3: U9.12 (IN3P); also elsewhere on the board
/ADS1299/AIN4: U9.10 (IN4P); also elsewhere on the board
/ADS1299/AIN5: U9.8 (IN5P); also elsewhere on the board
/ADS1299/AIN6: U9.6 (IN6P); also elsewhere on the board
/ADS1299/AIN7: U9.4 (IN7P); also elsewhere on the board
/ADS1299/AIN8: U9.2 (IN8P); also elsewhere on the board
/ADS1299/BIAS_INV: U9.61 (BIASINV); also elsewhere on the board
/ADS1299/BIAS_OUT: U9.63 (BIASOUT); also elsewhere on the board
/ADS1299/GPIO_1: J5.1, U9.42 (GPIO1)
/ADS1299/GPIO_2: J5.2, U9.44 (GPIO2)
/ADS1299/GPIO_3: J5.3, U9.45 (GPIO3)
/ADS1299/GPIO_4: J5.4, U9.46 (GPIO4)
/ADS1299/MISO: U9.43 (DOUT); also elsewhere on the board
/ADS1299/MOSI: U9.34 (DIN); also elsewhere on the board
/ADS1299/REF: U9.17 (SRB1); also elsewhere on the board
/ADS1299/SCK: U9.40 (SCLK); also elsewhere on the board
/ADS1299/nCS: R33.1, U9.39 (~CS); also elsewhere on the board
GNDA: C44.1, C45.2, C47.1, C48.1, C49.2, C50.1, C51.2, J5.6, R32.2, U9.31 (RESV1), U9.33 (DGND), U9.41 (DAISY_IN), U9.49 (DGND), U9.51 (DGND), U9.64 (RESERVED); also elsewhere on the board
unnamed: C42.2, C43.2, U9.24 (VREFP)
unnamed: C46.1, U9.26 (VCAP4)
unnamed: C52.1, C53.1, U9.55 (VCAP3)
unnamed: C54.1, U9.30 (VCAP2)
unnamed: C55.1, U9.28 (VCAP1)
unnamed: R32.1, U9.38 (START)
unnamed: R35.1, U9.52 (CLKSEL)
unnamed: R36.1, U9.35 (~PWDN)

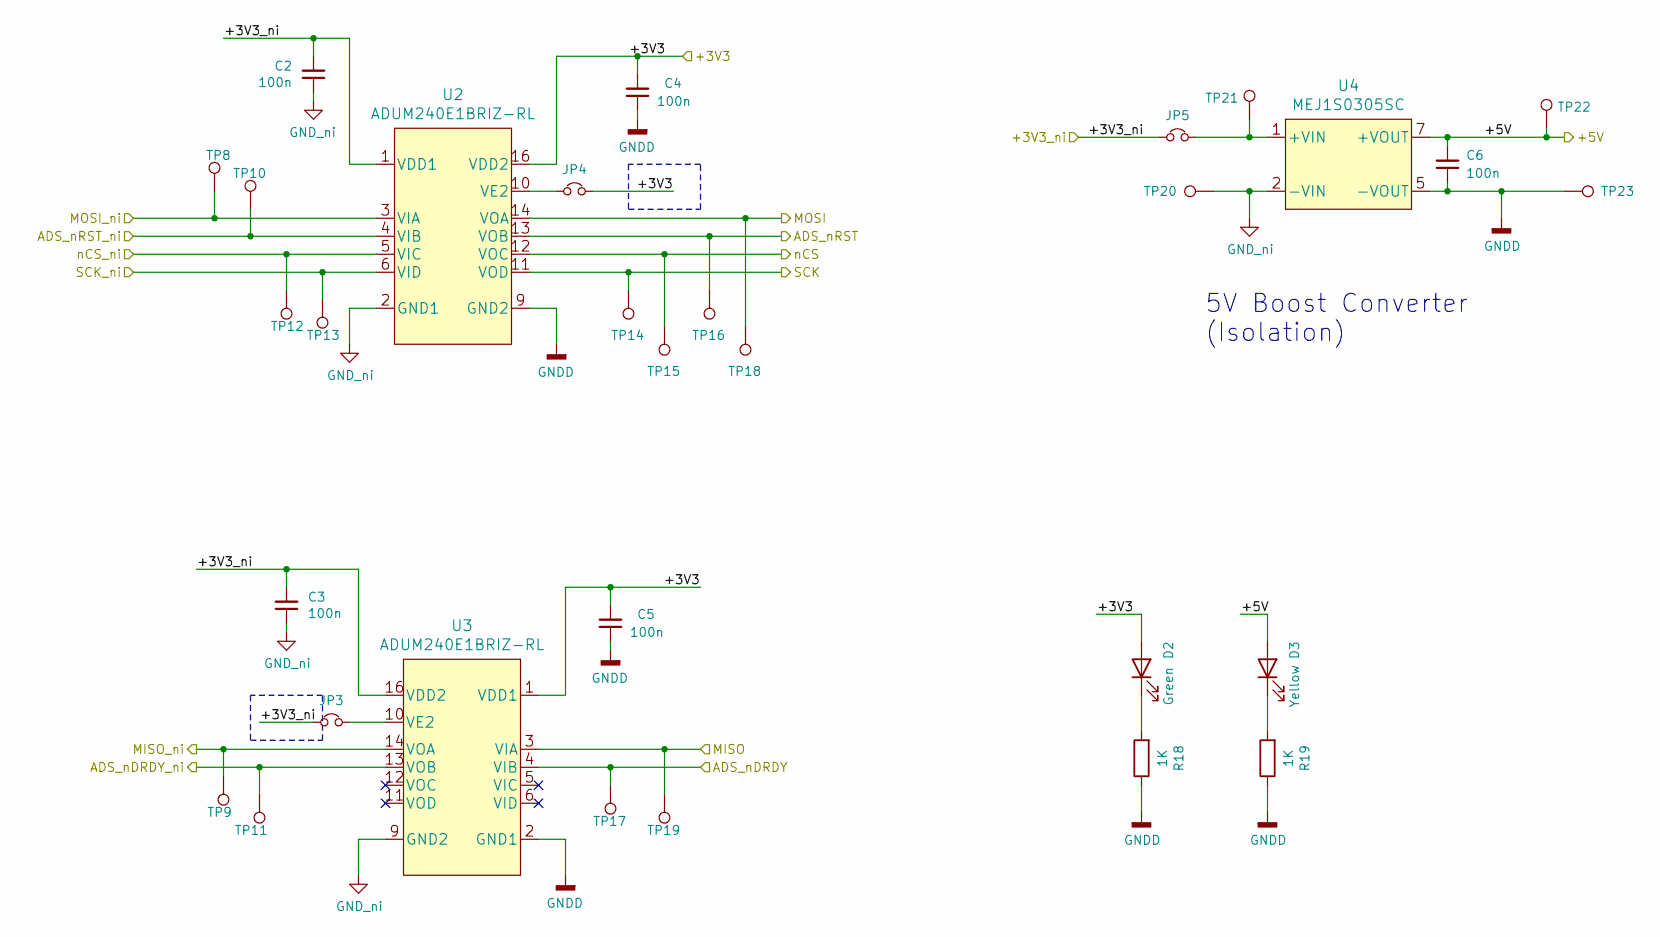
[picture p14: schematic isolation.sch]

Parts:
C2, C3, C4, C5, C6: 100n; C_0603_1608Metric_Pad1.08x0.95mm_HandSolder; Part Number CL21B104KACNNNC
D2: Green; LED_0603_1608Metric_Pad1.05x0.95mm_HandSolder; Part Number VFHL1116P-4BX3C-TR
D3: Yellow; LED_0603_1608Metric_Pad1.05x0.95mm_HandSolder; Part Number VFHY1104P-4C42D-TR
JP3, JP4, JP5: Jumper_NC_Small; SolderJumper-2_P1.3mm_Bridged_Pad1.0x1.5mm; Part Number N/A
R18, R19: 1K; R_0603_1608Metric_Pad0.98x0.95mm_HandSolder; Part Number RMCF0603FG1K00
TP8, TP9, TP10, TP11, TP12, TP13, TP14, TP15, TP16, TP17, TP18, TP19, TP20, TP21, TP22, TP23: TestPoint; TestPoint_Keystone_5010-5014_Multipurpose; Part Number N/A
U2, U3: ADUM240E1BRIZ-RL; SOIC-16W_7.5x12.8mm_P1.27mm; Part Number ADUM240E1BRIZ-RL
U4: MEJ1S0305SC; 7SIP; Part Number MEJ1S0305SC

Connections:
/ADS1299 Power/+3V3: C4.2, C5.2, D2.2 (A), JP4.2, U2.16 (VDD2), U3.1 (VDD1); also elsewhere on the board
/ADS1299 Power/+5V: C6.2, D3.2 (A), TP22.1, U4.7 (+VOUT); also elsewhere on the board
/ADS1299/ADS_nDRDY: TP17.1, U3.4 (VIB); also elsewhere on the board
/ADS1299/ADS_nRST: TP16.1, U2.13 (VOB); also elsewhere on the board
/ADS1299/MISO: TP19.1, U3.3 (VIA); also elsewhere on the board
/ADS1299/MOSI: TP18.1, U2.14 (VOA); also elsewhere on the board
/ADS1299/SCK: TP14.1, U2.11 (VOD); also elsewhere on the board
/ADS1299/nCS: TP15.1, U2.12 (VOC); also elsewhere on the board
/Isolation/+3V3_ni: C2.2, C3.2, JP3.1, JP5.1, U2.1 (VDD1), U3.16 (VDD2); also elsewhere on the board
/Isolation/MISO_ni: TP9.1, U3.14 (VOA); also elsewhere on the board
/Isolation/MOSI_ni: TP8.1, U2.3 (VIA); also elsewhere on the board
/Isolation/SCK_ni: TP13.1, U2.6 (VID); also elsewhere on the board
/nRF52840 Feather Sense Express Board/ADS-nCS_ni: TP12.1, U2.5 (VIC); also elsewhere on the board
/nRF52840 Feather Sense Express Board/ADS-nDRDY_ni: TP11.1, U3.13 (VOB); also elsewhere on the board
/nRF52840 Feather Sense Express Board/ADS-nRST_ni: TP10.1, U2.4 (VIB); also elsewhere on the board
GND: C2.1, C3.1, TP20.1, U2.2 (GND1), U2.8 (GND1), U3.9 (GND2), U3.15 (GND2), U4.2 (-VIN); also elsewhere on the board
GNDD: C4.1, C5.1, C6.1, R18.1, R19.1, TP23.1, U2.9 (GND2), U2.15 (GND2), U3.2 (GND1), U3.8 (GND1), U4.5 (-VOUT); also elsewhere on the board
unnamed: D2.1 (K), R18.2
unnamed: D3.1 (K), R19.2
unnamed: JP3.2, U3.10 (VE2)
unnamed: JP4.1, U2.10 (VE2)
unnamed: JP5.2, TP21.1, U4.1 (+VIN)

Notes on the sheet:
5V Boost Converter (Isolation)

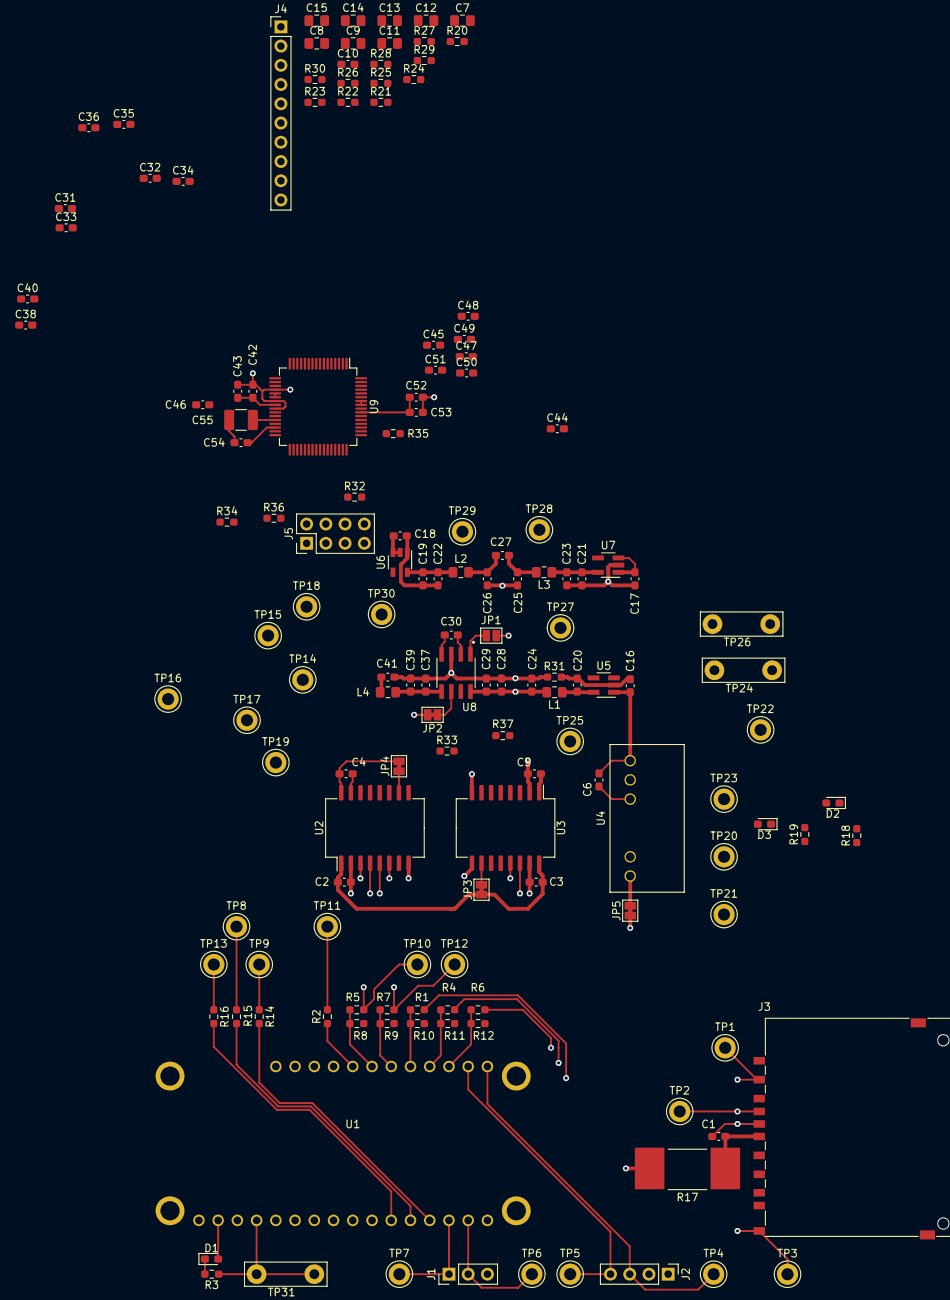
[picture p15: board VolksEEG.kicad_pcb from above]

Board: 4 copper layers, 148 parts (0 on the bottom side), 85 nets.

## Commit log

2021-04-23 Added power supply photo
2021-08-04 PCB: add Altium project
    [Footprint Library.PcbLib, Symbol Library.SchLib, VolksEEG.PcbDoc, VolksEEG.PrjPcb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]
2021-10-02 ADS, nRF, electrodes added to lib and sch
    [ADS1299.SchDoc, EEG-Electrodes.SchDoc, Footprint Library.PcbLib, Power.SchDoc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]
2021-10-02 pcb directory restructurated
    [ADS1299.SchDoc, EEG-Electrodes.SchDoc, Power.SchDoc, VolksEEG.PcbDoc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]
2021-10-02 Input and inverting power supply added
    [ADS1299.SchDoc, Power.SchDoc, VolksEEG.PrjPcb, nRF52840.SchDoc]
2021-10-02 OuputJob file added and BOM generated
    [VolksEEG.PrjPcb]
2021-10-05 Progress in transfer Altium to KiCAD
    [ADS1299.sch, EEG-Electrodes.sch, Power.SchDoc, Power.sch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]
2021-10-07 power supply finished
    [ADS1299.sch, Power.sch, VolksEEG.sch]
2021-10-10 pcb layout update
    [ADS1299.sch, EEG-Electrodes.sch, Power.sch, VolksEEG.kicad_pcb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]
2021-10-22 Started adding schematic sheet for isolation.
    [ADS1299.sch, EEG-Electrodes.sch, Power.sch, VolksEEG.sch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]
2021-10-22 re-organised the root schematic, plumbed in the power and signal lines. renamed the nrf52840 sheet to highlight the fact it is the Feather Sense Express board.
    [VolksEEG.sch]
2021-10-23 Some re-naming and added some pull ups to the nrf schematic.
    [VolksEEG.sch, isolation.sch, nRF52840.sch]
2021-10-23 Added Digi-key's kicad component libraries, some work done on power, think this will change but capturing it here for posterity.
    [ADS1299.sch, Power.sch, VolksEEG.sch, isolation.sch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]
2021-10-23 Rejigged the power around so that the 3v3 supply is only generated once.
    [Power.sch, VolksEEG.sch, isolation.sch]
2021-10-25 Updating analogue inputs to the referential montage and connected a few ADS1299 pins.
    [ADS1299.sch, EEG-Electrodes.sch, VolksEEG.sch, isolation.sch]
2021-10-26 Added list of known remaining tasks on the schematic.
    [VolksEEG.sch]
2021-10-26 Added more tasks following re-watch of 1st half of previous design review.
    [VolksEEG.sch, isolation.sch, nRF52840.sch]
2021-10-26 Updated names of heirarchical pins, finished referential montage configuration, added filter cap to ADS_nRST line, started putting ADS1299 gpios to a header.
    [ADS1299.sch, EEG-Electrodes.sch, Power.sch, VolksEEG.sch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]
2021-10-26 Added custom power symbols for non isolated power. Seperated Analogue and digital supplies. finished putting the ADS1299 GPIOs to a header.
    [ADS1299.sch, EEG-Electrodes.sch, Power.sch, VolksEEG.sch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]
2021-10-27 Tweaks based on feedback, Changed digital isolators to ADUM240E devices due to component availability.
    [ADS1299.sch, Power.sch, VolksEEG.sch, isolation.sch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]
2021-10-27 Changed -2.5V Regulator due to part availability.
    [Power.sch]
2021-10-27 Added debugging bits to the NRF schematic sheet.
    [VolksEEG.sch, nRF52840.sch]
2021-10-28 Added debugging bits to more schematic sheets.
    [ADS1299.sch, EEG-Electrodes.sch, Power.sch, VolksEEG.sch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]
2021-10-28 tweaks to the ADS1299 schematic.
    [ADS1299.sch, EEG-Electrodes.sch]
2021-10-29 finished off tasks list.
    [ADS1299.sch, Power.sch, VolksEEG.sch]
2021-11-02 Removed deprecated Altium files.
    [ADS1299.SchDoc, EEG-Electrodes.SchDoc, Power.SchDoc, VolksEEG.PcbDoc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]
2021-11-02 Changed ADuM420 sch symbol to more KiCAD-like look.
    [isolation.sch]
2021-11-02 Changed MEJ1S sch symbol to be more KiCAD-like.
    [Power.sch, isolation.sch]
2021-11-14 Cleaned up nrf page and converted +3V3_ni to non-global symbols.
    [isolation.sch, nRF52840.sch]
2021-11-14 Updated schem symbol for ADP7182.
    Converted symbol to be more KiCAD-like.
    This includes stacking the pins, removing the NC pins, and making the background yellow.
    [Power.sch]
2021-11-14 Fixed an bug with the global power nets being used.
    The use of global power nets caused the +3V3A, +3V3, and -3V3A nets to be shorted together.
    [ADS1299.sch, Power.sch, isolation.sch]
2021-11-14 Updated schem symbols on Power sheet.
    Updated symbols to remove NC pins.
    Updated pcb footprints to use default SOT-23-5 rather than custom footprint, and deleted custom footprint.
    [ADS1299.sch, Power.sch]
2021-11-14 Removed custom global power symbols to prevent the bug from happening again.
    [Power.sch, isolation.sch]
2021-11-14 Annotated schematic and cleared ERC errors.
    [ADS1299.sch, EEG-Electrodes.sch, Power.sch, VolksEEG.sch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]
2021-11-14 Cleaned up ADS1299 page.
    [ADS1299.sch]
2021-11-15 General schematic cleanup, and assigning some footprints.
    Cleaning up the meta-data within KiCAD, and assigning some basic footprints.
    Also, cleaning out some footprint references that didn't point anywhere.
    [ADS1299.sch, Power.sch, isolation.sch, nRF52840.sch]
2021-11-15 Change ADS1299 over to using the KiCAD library footprint.
    Also deleted the custom drawn QFP footprint.
    [ADS1299.sch, Power.sch, isolation.sch]
2021-12-11 Updated some footprints and part manufacturers and numbers.
    [ADS1299.sch, EEG-Electrodes.sch, Power.sch, isolation.sch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]
2021-12-12 Finished adding footprints, and started laying out the isolation section.
    [ADS1299.sch, EEG-Electrodes.sch, Power.sch, VolksEEG.kicad_pcb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]
2021-12-15 Layout of the NRF52840 section of the PCB.
    [Power.sch, VolksEEG.kicad_pcb, isolation.sch, nRF52840.sch]
2022-01-09 Further PCB Layout.
    [ADS1299.sch, Power.sch, VolksEEG.kicad_pcb]
2022-04-09 Added initial work on Dev board.
    [DevBoard-B_Cu.gbr, DevBoard-B_Mask.gbr, DevBoard-B_Paste.gbr, DevBoard-B_Silkscreen.gbr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]
2022-04-09 Added revision and 'Not for use as a medical device' to the silkscreen.
    [DevBoard-B_Cu.gbr, DevBoard-B_Mask.gbr, DevBoard-B_Paste.gbr, DevBoard-B_Silkscreen.gbr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]
2022-04-10 adjusted board dimensions slightly and regenerated Gerbers.
    [DevBoard-B_Cu.gbr, DevBoard-B_Mask.gbr, DevBoard-B_Paste.gbr, DevBoard-B_Silkscreen.gbr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]
2022-07-13 Fixed some net names on schematic
    [DevBoard-B_Cu.gbr, DevBoard-B_Mask.gbr, DevBoard-B_Paste.gbr, DevBoard-B_Silkscreen.gbr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]
2022-07-13 Updates
    WIP
    [DevBoard-B_Cu.gbr, DevBoard-B_Mask.gbr, DevBoard-B_Paste.gbr, DevBoard-B_Silkscreen.gbr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]
2022-07-13 Ready for schematic review
    Besides changing net names and so forth:
    - Changed Feather 3V pin to output
    - Added ADS1299EEGFE-PDK to VolksEEG symbol library
    - Added Adafruit_SD_Breakout to VolksEEG symbol library
    ERC complains that three switches should be updated from library, can't seem to fix that
    [DevBoard.kicad_pcb]
2022-07-13 Added video of prototype UI
2022-07-13 Revert "Added video of prototype UI"
    This reverts commit 8652e89c198d57db21fe4f76202bbbf2b087be41.
2022-07-13 As sent to JLBPC
    [DevBoard.kicad_pcb, DevBoard.kicad_sch]
2022-07-13 Cleared out KiCAD backups, and added .gitignore for dev boards.
